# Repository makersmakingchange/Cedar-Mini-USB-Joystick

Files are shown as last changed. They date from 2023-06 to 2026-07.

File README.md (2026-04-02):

# Cedar Mini USB Joystick

## Overview

The Cedar Mini USB Joystick is a mini sized proportional joystick with integrated switch ports that can act as either an HID gamepad or as a mouse for adaptive gaming or computer access. Based on a generic PS2-style game controller thumbstick, it has range of motion of ±30° and requires approximately 75 grams-force to fully deflect. This joystick has a USB output cable and 3 ports for external assistive switches. 

The Cedar Mini USB Joystick can be used directly as a left or right thumbstick for the [Microsoft Xbox Adaptive Controller (XAC)](https://www.xbox.com/en-CA/accessories/controllers/xbox-adaptive-controller) using the Left and Right USB joystick ports in Joystick mode, or directly with a computer or mobile device.

A range of toppers are available for this joystick, including a [set of toppers created by AbleGamers Charity](https://www.printables.com/model/501869-analog-thumbstick-topper-collection).
 
The Cedar Mini USB Joystick is open assistive technology (OpenAT). Under the terms of the open source licenses, the device may be built, used, and improved upon by anyone.

The overall cost of materials is about $43 CAD (plus $8 CAD for component shipping).

The [Spruce Mini Joystick](https://github.com/makersmakingchange/Spruce-Mini-Joystick) is an alternative version of this joystick. It uses the same thumbstick component, but instead of USB output it has a TRRS cable for the joystick and a mono cable for the integrated joystick button. 

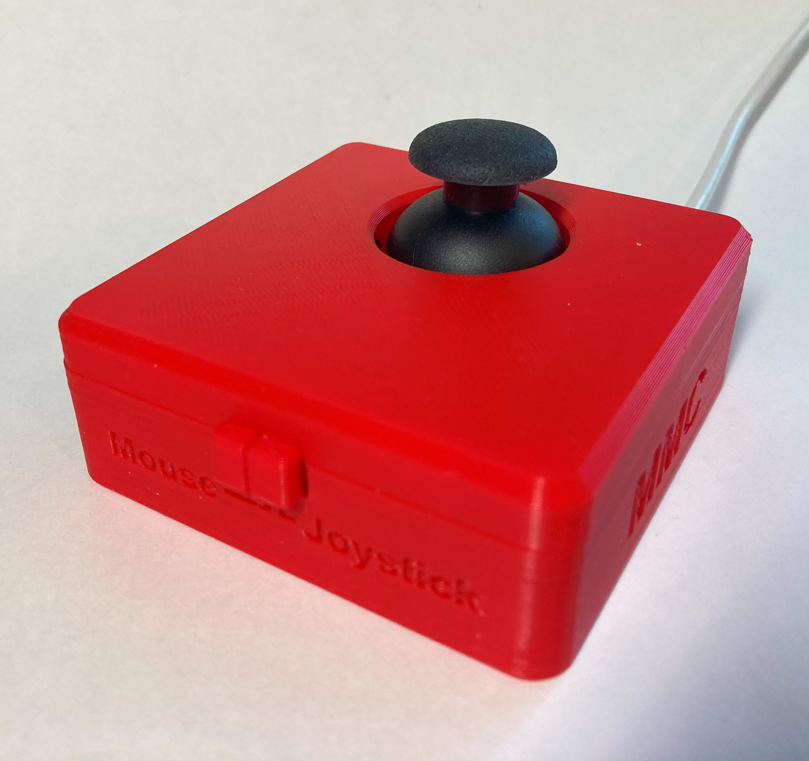
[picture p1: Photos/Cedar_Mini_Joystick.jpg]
Picture of Cedar Mini USB Joystick.


## Makers Making Change Assistive Device Library
https://www.makersmakingchange.com/s/product/cedar-mini-usb-joystick/01tJR00000092vRYAQ

## OpenAT Joysticks
This design is part of the [OpenAT Joystick project](https://github.com/makersmakingchange/OpenAT-Joysticks), a collection of open source designs for digital access and adapted gaming.  

## How to Obtain the Device
### 1. Do-it-Yourself (DIY) or Do-it-Together (DIT)

This is an open-source assistive technology, so anyone is free to build it. All of the files and instructions required to build the device are contained within this repository. Refer to the Maker Guide below.

### 2. Request a build of this device

You may also submit a build request through the [Makers Making Change Assistive Device Library Listing](https://www.makersmakingchange.com/s/product/cedar-mini-usb-joystick/01tJR00000092vRYAQ) to have a volunteer maker build the device. As the requestor, you are responsible for reimbursing the maker for the cost of materials and any shipping.

### 3. Build this device for someone else

If you have the skills and equipment to build this device, and would like to donate your time to create the device for someone who needs it, visit the [MMC Maker Wanted](https://makersmakingchange.com/maker-wanted/) section.

## Build Instructions
<!--- Outline the major steps required to create a build --->

### 1. Read through the Maker Guide

The [Maker Guide](/Documentation/Cedar_Joystick_Maker_Guide.pdf)  contains all the necessary information to build this device, including tool lists, assembly instructions, programming instructions (if applicable) and testing.

### 2. Order the Off-The-Shelf Components

The [Bill of Materials](/Documentation/Cedar_Joystick_BOM.csv) lists all of the parts and components required to build the device.

### 3. Print the 3D Printable components

All of the files and individual print files can be found in the [/Build_Files/3D_Printing_Files](/Build_Files/3D_Printing_Files/) folder.

Make sure to ask the user if they would like any of the optional prints such as toppers or mount adapters. Refer to the [OpenAT Joystick Setup Guide](https://github.com/makersmakingchange/OpenAT-Joysticks/Resources/OpenAT_Joystick_Setup_Guide.pdf) for detailed mounting options. 

### 4. Assemble the Cedar Mini USB Joystick

Reference the Assembly Guide section of the [Maker Guide](/Documentation/Cedar_Joystick_Maker_Guide.pdf) for the tools and steps required to build the device.

## How to improve this Device
As open source assistive technology, you are welcomed and encouraged to improve upon the design. 

## Files
### Documentation
<!--- Update the name, link, and version for documentation --->
| Document             | Version | Link |
|----------------------|---------|------|
| Design Rationale     | 1.0     | [Cedar_Joystick_Design_Rationale](/Documentation/Cedar_Joystick_Design_Rationale.pdf)     |
| Maker Guide          | 1.0     | [Cedar_Joystick_Maker_Guide](/Documentation/Cedar_Joystick_Maker_Guide.pdf)     |
| Bill of Materials    | 1.0     | [Cedar_Joystick_Bill_of_Materials](/Documentation/Cedar_Joystick_BOM.csv)     |
| User Guide           | 1.0     | [Cedar_Joystick_User_Guide](/Documentation/Cedar_Joystick_User_Guide.pdf)    |
| Changelog            | 1.0     | [Changelog](CHANGES.txt)     |

### Design Files
<!--- Include a copy of the original design files to facilitate easy editing and customization. Consider also including a generic format (e.g., STEP) --->
 - [CAD Files](/Design_Files/CAD_Design_Files)

### Build Files
<!--- Include a copy of the build files intended for manufacturing. This may include svg files for laser cutting, stl files for 3d printing, Gerber files for custom PCBs, and Arduino files for custom firmware. --->
 - [3D Printing Files](/Build_Files/3D_Printing_Files)
 - [Firmware Files](/Build/Firmware_Files)

## License
Copyright (c) 2023-2026 Neil Squire Society.

This repository describes Open Hardware:
 - Everything needed or used to design, make, test, or prepare the Cedar Mini USB Joystick is licensed under the [CERN 2.0 Weakly Reciprocal license (CERN-OHL-W v2) or later](https://cern.ch/cern-ohl ) .
 - All software is under the [GNU General Public License v3.0 (GPL-3.0)](https://www.gnu.org/licenses/gpl.html).
<<<<<<< Updated upstream
 - Accompanying material such as instruction manuals, videos, and other copyrightable works that are useful but not necessary to design, make, test, or prepare the Cedar USB Joystick are published under a [Creative Commons Attribution-ShareAlike 4.0 license (CC BY-SA 4.0)](https://creativecommons.org/licenses/by-sa/4.0/) .
=======
 - Accompanying material such as instruction manuals, videos, and other copyrightable works that are useful but not necessary to design, make, test, or prepare the Cedar Joystick are published under a [Creative Commons Attribution-ShareAlike 4.0 license (CC BY-SA 4.0)](https://creativecommons.org/licenses/by-sa/4.0/) .
>>>>>>> Stashed changes

You may redistribute and modify this documentation and make products using it under the terms of the [CERN-OHL-W v2](https://cern.ch/cern-ohl).
This documentation is distributed WITHOUT ANY EXPRESS OR IMPLIED WARRANTY, INCLUDING OF MERCHANTABILITY, SATISFACTORY QUALITY AND FITNESS FOR A PARTICULAR PURPOSE.
Please see the CERN-OHL-W v2 for applicable conditions.

Source Location: https://github.com/makersmakingchange/Cedar-Mini-USB-Joystick 

## Attribution
<!--- Provide any necessary attribution for designs or components that are included in the device or as part of the project. --->
The device was designed by the Neil Squire Society / Makers Making Change Program. 

The software utilizes the [Adafruit TinyUSB Library for Arduino](https://github.com/adafruit/Adafruit_TinyUSB_Arduino) which is made available under an [MIT license](https://github.com/adafruit/Adafruit_TinyUSB_Arduino/blob/master/LICENSE).

A range of toppers are availablef or this joystick and utilize the mofels found in the [set of toppers created by AbleGamers Charity](https://www.printables.com/model/501869-analog-thumbstick-topper-collection).

<!--- This is the attribution for the template. --->
This project uses the documentation template created by Neil Squire Society / Makers Making Change. It is available at the following link: [https://github.com/makersmakingchange/OpenAT-Template](https://github.com/makersmakingchange/OpenAT-Template)

### Contributors
<!--- List the names of the people that contributed to the design. This could include the original source of the idea, designers, testers, documenters, etc. --->
Designers:
 - Josie Versloot, Neil Squire Society. Hardware and enclosure design, software, documentation.
 - Milad Hajihassan, Neil Squire Society. Software.
 - Emily Schwitz, Neil Squire Society. Documentation.
 - Tyler Fentie. Documentation, Editing.
 - Jake McIvor. Documentation, testing, editing.

---
<!--- This is standard boilerplate for Makers Making Change. No changes should be required. --->
<!-- ABOUT MMC START -->
## About Makers Making Change
[Makers Making Change Logo](https://www.makersmakingchange.com/)

Makers Making Change is a program of [Neil Squire](https://www.neilsquire.ca/), a Canadian non-profit that uses technology, knowledge, and passion to empower people with disabilities.

Makers Making Change leverages the capacity of community based Makers, Disability Professionals and Volunteers to develop and deliver affordable Open Source Assistive Technologies.

 - Website: [www.MakersMakingChange.com](https://www.makersmakingchange.com/)
 - GitHub: [makersmakingchange](https://github.com/makersmakingchange)
 - Bluesky: [@makersmakingchange.bsky.social](https://bsky.app/profile/makersmakingchange.bsky.social)
 - Instagram: [@makersmakingchange](https://www.instagram.com/makersmakingchange)
 - Facebook: [makersmakechange](https://www.facebook.com/makersmakechange)
 - LinkedIn: [Neil Squire Society](https://www.linkedin.com/company/neil-squire-society/)
 - Thingiverse: [makersmakingchange](https://www.thingiverse.com/makersmakingchange/about)
 - Printables: [MakersMakingChange](https://www.printables.com/@MakersMakingChange)

### Contact Us
For technical questions, to get involved, or to share your experience we encourage you to [visit our website](https://www.makersmakingchange.com/) or [contact us](https://www.makersmakingchange.com/s/contact).
<!-- ABOUT MMC END -->

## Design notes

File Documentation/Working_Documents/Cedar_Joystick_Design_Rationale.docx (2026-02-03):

# Overview

The Design Rationale is intended to provide designers and maker information about the design process and design decisions behind the development of the Cedar USB Joystick, a joystick with switch ports.

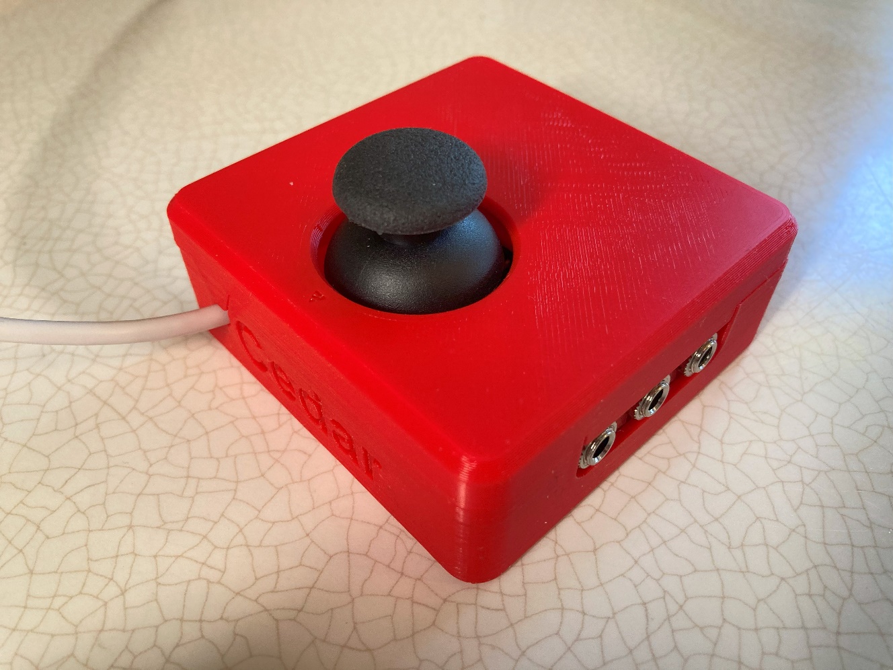
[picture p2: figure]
A photo of a fully assembled Cedar USB Joystick.

# Contents

# Introduction

There is an identified need for cost-effective analog joysticks that can be used with the Xbox Adaptive Controller (XAC). There are currently not very many commercial joysticks on the market, and the ones that are can be costly. This joystick is intended to be used with the XAC for anyone who may find it easier to game with a joystick.

There is also a need for alternative mouse options that are affordable, and some people may find a joystick easier to use than a mouse. This mouse needs to be a standalone device that can be used with PC and can complete the basic mouse functions such as left click.

This joystick specifically is meant for someone with a lower range of motion and lower force compared to some USB joysticks.

# Research

## Commercial Joysticks:

Name | Price | | Link | | | Picture
Ultra-Stik | 95 UK | | Accessible Gaming Shop - Ultra-Stik - OneSwitch.org.uk (https://www.oneswitch.org.uk/art.php?id=17)
XAC MINI Stick | 105 UK | | XAC Mini Joystick - OneSwitch.org.uk (https://www.oneswitch.org.uk/art.php?id=270)
Optima Joystick | 219.60 UK | | Optima Joystick - Video Gaming Assistive Joystick (pretorianuk.com) (https://www.pretorianuk.com/optima-joystick)
PDP One-Handed Joystick for Xbox Adaptive Controller | Out of Stock | | PDP One-Handed Joystick for Xbox Adaptive Controller (microsoft.com) (https://www.microsoft.com/en-ca/d/pdp-one-handed-joystick-for-the-xbox-adaptive-controller/8qhw8mlwpp1l)
XAC Flat Thumbstick | $74.95 | | XAC Flat Thumbstick (evilcontrollers.com) (https://www.evilcontrollers.com/xac-flat-thumbstick)
Name | | Price | | Link | Picture
MINISTIX-TU | | $75 | | MINISTIX-TU (USB Version) — Warfighter Engaged (https://warfighterengaged.org/shop/ministix-tu)
DPAD-T | | $65 | | DPAD-T — Warfighter Engaged (https://warfighterengaged.org/shop/dpad-t)
JOYSTIX-FPS | | $75 | | JOYSTIX-FPS — Warfighter Engaged (https://warfighterengaged.org/shop/joystix-l-aenef)
JoyCon® Style Joystick For XBOX® Adaptive Controller & PC (JoyToKey) | | $60.40 | | Joycon® Style Joystick for XBOX® Adaptive Controller & PC | Etsy Canada (https://www.etsy.com/ca/listing/1205880837/joycon-style-joystick-for-xbox-adaptive?click_sum=ba40a784&crt=1)

# Ideation

## Joystick Element

For this design, the same joystick element will be used as the current Analog Thumbstick on the website, which is a standard PS2 thumbstick unit.

## Switch Input

There are a few different ways that switch input can be accomplished:

- Integrated buttons
- Integrated switch jacks
- Separate “controller box” that the joystick and switches plug into

For this design, it was decided to use integrated switch jacks, where the user can plug in their assistive switch of choice for switch input. While in mouse mode, these switches will be left click, right click, and middle click (scroll).

This decision will be further investigated and specifically asked about in user testing.

# Conceptual Design

## Electrical Design

### Microcontroller

The microcontroller used in this design is the Adafruit QT Py SAMD21.

Originally the Seeed Studio XIAO RP2040 was going to be used since it is the microcontroller used in the Oak Compact Joystick – U and the Birch Mini joystick – U, but during development and testing there were problems reading the switch inputs. From what we read online; this was likely due to the pullup resistors. Documentation for the XIAO RP2040 is not consistent, some sources say it has pullup resistors and others say it does not. After this realization, both the Adafruit QT Py SAMD21 board and the Seeed Studio XIAO SAMD21 boards were tested since they both have the same footprint as the XIAO RP2040 board. The Seeed Studio XIAO SAMD21 board had problems with the Adafruit TinyUSB library, after looking online this is a known problem, but the solution of using an older version of the TinyUSB library did not work either. The Adafruit QT Py SAMD21 board, however, seemed to work well, so the final decision was to use this board even though on Digikey it is approximately $3 more.

### Switch Inputs

This design will use switch jacks integrated into the body of the joystick. There will be 3 switch jacks, which in mouse mode will represent left click, right click, and middle click.

From initial conversations with clinicians and users, it was determined that these three inputs are all very important. The ability to easily scroll is sometimes overlooked but the importance of this was expressed to us, so this will be accomplished through the middle click button.

### Mode Switch

A 3-way slide switch to switch between mouse mode and joystick mode, will also be included in this design. This is so that either the user or secondary user (such as a support person) can easily change the mode to use this joystick as either a joystick or mouse. This method of mode switching does not require the user or secondary user to have any knowledge of code or software, and allows this mode switch to happen easier than if the joystick and mouse used separate versions of the code.

The selection of which switch exactly will be used will depend on the method of electronical component mounting and wiring, decided below. This will dictate whether the slide switch needs to be panel mounted, breadboard friendly, right angled, etc.

Example of a breadboard friendly slide switch:

https://www.adafruit.com/product/805

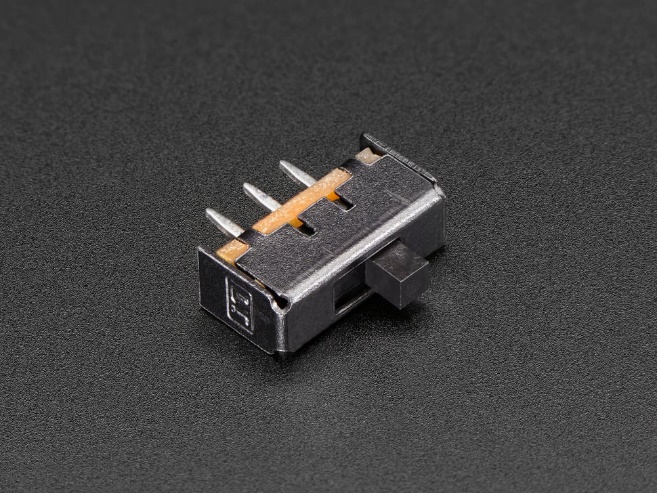
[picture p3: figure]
Breadboard-friendly SPDT Slide Switch

### Electrical Component Wiring and Mounting

For mounting the electrical components and wiring the components together, there are a few options to accomplish this:

1. Components mounted directly in 3D printed enclosure (panel mount switch jacks and slide switch)
2. 3D printed PCB/3D printed jig
3. Protoboard with breadboard friendly jacks
4. Combination of protoboard and panel mounts
5. Printed Circuit Board (PCB)

With each of these options there are a few different factors to consider:

- Ease of assembly for the maker
- Device cost
- Design complexity
- Device size

For each of these concepts the following components need to be included:

- Microcontroller
- Joystick Module
- 3x Switch Jack
- Slide Switch

#### Concept 1: Components mounted directly in 3D printed enclosure

This would use panel mount components for the slide switch and switch jacks, and would involve mounting the microcontroller directly in the enclosure. Wiring would be completed with free floating wires.

Easy of assembly: a lot of free floating wires, tricky to hold while soldering, tricky to keep them all straight, would need to daisy chain multiple ground wires together. If soldering while the components are mounted it could be hard to get in to solder, but if the components are free there is risk the wires may not reach.

Device cost: lower cost due to not having to buy protoboard or a PCB. Other components similar in price.

Design complexity: easy to design, easy to mount components where they fit best. Will need to consider how to mount the micro controller.

Device size: allows the device to be relatively compact since components can be placed anywhere in the enclosure that thy fit best.

#### Concept 2: 3D printed PCB/3D printed jig

This would involved a 3D printed board that the components would be mounted to and would help guide the wiring.

This could be similar to the Switch Input Module for the LipSync:

Female headers could be embedded in the 3D print for mounting the microcontroller and this could help guide the wires for connecting the switch jacks and slide switch to the microcontroller, and would likely be easier than free hanging wires. The switch jacks, slide switch, and microcontroller could all be mounted on this board, and the board could have any shape needed to fit in the enclosure and fit around the joystick component. There could be female headers that fit onto the male headers on the joystick board.

Ease of assembly: Likely easier than free hanging wires in Concept 1, but more complex than a PCB. The print would help guide the positioning and wiring of the various components.

Device cost: lower cost due to not having to buy protoboard or a PCB. Other components similar in price.

Design complexity: Relatively complex, positioning and wiring of each component needs to be considered in the board. Pieces need to fit properly.

Device size: allows the device to be compact since the printed board can take on any necessary shape.

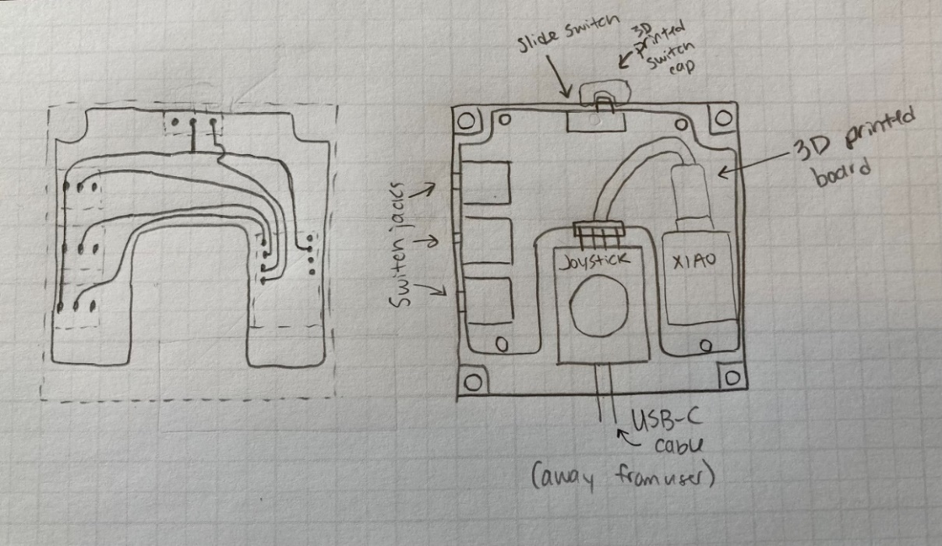
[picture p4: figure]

This concept was also tested out in CAD to see the real size of components relative to each other. This was the first attempt at laying out the components:

#### Concept 3: Protoboard with breadboard friendly jacks

Ease of assembly: Likely easier than concept 1 with the panel mounted components and free floating wires, and slightly easier than the 3D printed PCB, but likely somewhat comparable. If using stripboard, this will be more simple, but if using protoboard with individual pads this will be more complex as it will require solder bridges.

Device cost: Added cost of the protoboard. Depending on the board this could range from $2 to $6. Other components should be similar in price.

Design complexity: Relatively simple design, if the protoboard has screw holes these can be incorporated, otherwise will need to think about mounting the protoboard.

Device size: This depends on if using stripboard or single pad protoboard, but with stripboard as seen below space cannot be as optimized since the pads are connected, dictating where components can and cannot go. If using single pad protoboard, the design can be more compact, but this adds assembly complexity.

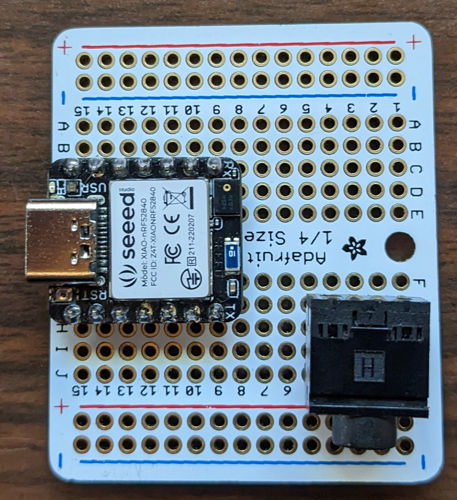
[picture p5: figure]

https://www.adafruit.com/product/589

3 breadboard friendly audio jacks could fit along one side of a quarter sized proto board, or the SeeedStudio XIAO board (same footprint as Adafruit AT Py) could fit along with 2 breadboard friendly audio jacks.

Another concept that was experimented with was using two protoboard with individual pads (rather than strip board) and attaching the two boards together using right angle male and female headers.

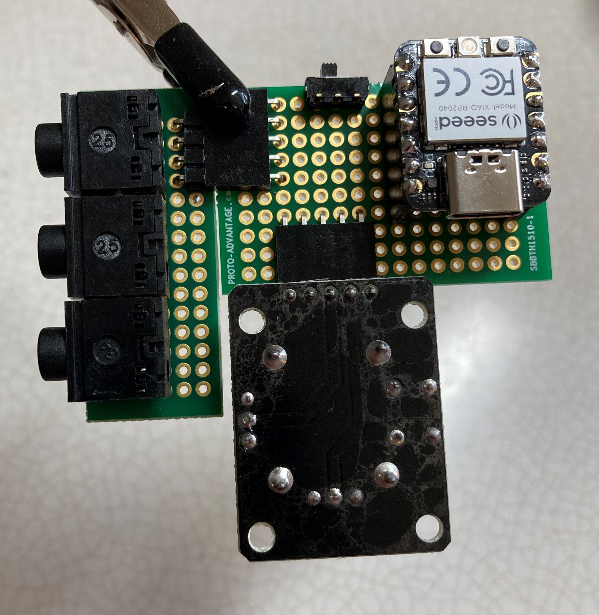
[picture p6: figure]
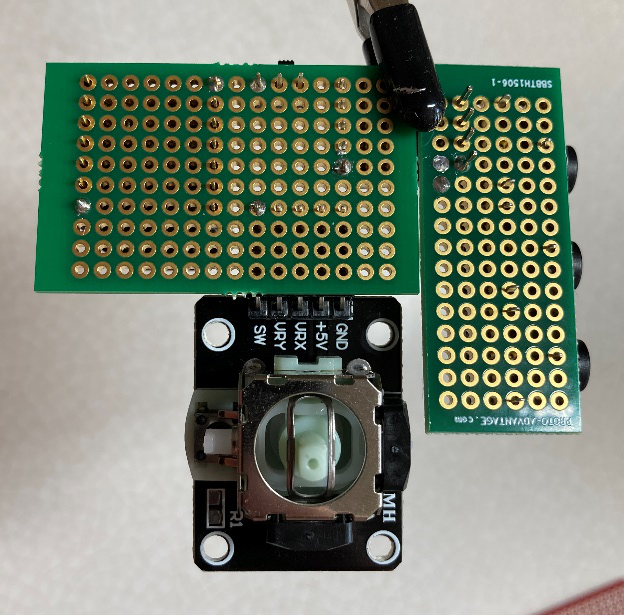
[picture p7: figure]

This concept has promise since it is relatively compact, and having the components on the “underside” of the protoboard decreases the height of the enclosure significantly. However, with these protoboards there is still the challenge of mounting them since they do not have screw holes, and they would need to be secure since the user would be plugging and unplugging switches from the mono jacks. Additionally, since it uses individual pads instead of stripboard, wiring would likely require solder bridges which means assembly would not be much easier than the 3D PCB.

#### Concept 4: Combination of protoboard and panel mounts

This concept would allow for the use of a smaller protoboard than concept 3, since not all components would need to be mounted on it. For example, the microcontroller and slide switch could mount to the protoboard and the mono jacks could be panel mounted. Another possibility is having the mono jacks and slide switch on the protoboard and then having the microcontroller mounted to the enclosure directly. This can also allow for a more compact layout than concept 3 if using one protoboard.

Ease of assembly: Slightly easier than concept 1 with all panel mounted components, but more difficult than concept 3 with a protoboard.

Device cost: Similar to concept 4, more than concept 1 and 2 due to added cost of protoboard.

Design complexity: Relatively simple, depending on the mounting of the protoboard.

Device size: Allows the enclosure to be more compact than concept 3 (if only using one board) since the layout of the parts is not defined by the size and layout of the protoboard.

#### Concept 5: Printed Circuit Board (PCB)

Ease of assembly: This would be the easiest of the options in terms of assembly, since the components could just be soldered to the board and wires would not need to be added between components. There would also be less room for error while assembling with this option.

Device cost: Adds approximately ~$30 to cost for a single build

Design complexity: It takes time to prototype, order, and test PCB boards, so the design complexity is likely too high for the timeline of the initial design.

Device size: A custom PCB can be made in any shape, therefore allowing the size to be relatively compact.

Discussion: One PCB design could be used across different devices.

#### Selection

For the initial version of this design, version 0.9, concept 2 with the 3D printed circuit board was selected. This option is easier to assemble than concept 1; lower cost than concept 3, 4, and 5; and is only marginally more difficult to assemble than concept 3. Though concept 5 would be easier to assemble, the cost is much higher, and the design time is not feasible for this design iteration.

There is a possibility of creating a PCB at a later stage in the design process, and having two options for the build depending on if someone is building one or multiple. When building multiple joysticks, the cost of the PCB per joystick drops significantly, making it a more viable option when doing bulk orders.

While designing the 3D printed circuit board, the idea of implementing concept 5 at a later date will be kept in mind, and the 3D printed circuit board will be designed to be able to easily transition to a custom ordered PCB at a later date.

## Firmware Design

For this joystick, the joystick mode and mouse mode will be captured on one firmware, with a slide switch to switch between modes. This switch will be checked once upon startup, and will determine if the device will be set up as a joystick/HID gamepad or as a mouse. If switching between joystick and mouse mode, the device will need to be unplugged and plugged back into the host device.

For both joystick and mouse output, there is a deadzone where if the joystick readings are below a certain value, the output will be zero. This code uses a radial deadzone, which if mapped would have a circular shape, and the radius of this deadzone is set in a variable at the start of the code. If the joystick is experiencing drift, this deadzone may need to be increased. If small movements are not corresponding to outputs, this value may need to be decreased.

### Joystick Mode

For the joystick mode portion of the code, the code from the MMC OpenAT Joysticks, the Birch Mini Joystick – U and the Oak Compact Joystick – U will be used and modified. The main changes from this code will be incorporating the switch inputs and modifying the code to work with the Adafruit QT Py SAMD21 microcontroller.

This joystick has three accessible switch jacks, and has one built in switch in the joystick that is activated when the joystick is pressed down. These switches will be mapped as buttons 1 to 4 on the gamepad output.

### Mouse Mode

For the mouse mode portion of the code, the mouse functions were added into the joystick code, with conditional statements so they are only outputted when in mouse mode. The three switch jacks (labelled A, B, C from left to right) are mapped as left click, middle click (for scroll), and right click (from left to right). The joystick press down button is mapped to left click.

Since the joystick portion of the code requires the use of the Adafruit TinyUSB stack, and the typical Mouse.h library uses the Arduino USB stack, an alternative library had to be used that allowed for Mouse functionality with the TinyUSB stack. This library was found on GitHub by user cyborg5 (https://github.com/cyborg5/TinyUSB_Mouse_and_Keyboard).

## Mechanical Design

The mechanical design is largely dependant on the electrical component wiring and mounting. After selecting concept 2 for the electrical design, the enclosure and 3D PCB could be designed. The current Analog Thumbstick on the MMC library has a footprint of 69 mm by 69 mm, so effort will be made for this new enclosure design to be similar in size.

In this enclosure, it will be ensured that the mono jacks and slide switch are mounted in a way that is very secure since the user will be applying forces to these parts.

The enclosure will also include captive M3 nuts to be used with the MMC Joystick camera mount adapter.

The current Analog Thumbstick on the MMC library uses 4 screws to secure the enclosure, and 4 screws to secure the joystick to the enclosure. This approach will be used for this enclosure as well, for both simplicity of design, and strength of the connection. Since the user will be applying forces to the joystick that could be quite large, this needs to be mounted to the enclosure in a strong and secure way. Relying on snap fits can also be difficult if printer tolerances are very different. This enclosure, like the Analog Thumbstick, will use 8 size 4-24 self threading sheet metal screws. The 3D PCB will be secured using the same screws as the ones holding together the enclosure.

# Minimum Viable Product – V0.9

## Summary

- Cost
  - Unit cost: $42.74 ($34.74 for parts, $8 shipping)
  - Total maker cost: $64.33 ($56.33 for parts, $8 shipping)
- Print time: 4 hours 53 mins
- Total 3D printer filament used: 41 g
- Approximate build time: 1 hour??
- Size:
  - Total Height: 4.0 cm with original topper
  - Enclosure height: 2.7 cm
  - Width: 7.0 cm
  - Length: 7.0 cm

### Bill of Materials

The following components were selected based on price, availability, and components used internally for MMC designs.

Part Name | QTY | QTY /PKG | $/PKG | PKG QTY | $/Unit | Extended | Total
Joystick (PS2) (https://www.amazon.ca/dp/B089VXPHDH?_encoding=UTF8&psc=1&ref_=cm_sw_r_cp_ud_dp_GGTEDME4PM2P27SG86P7) | 1 | 10 | $ 23.99 | 1 | $ 2.40 | $ 2.40 | $ 23.99
USB-C cable, 6 ft (https://www.digikey.ca/en/products/detail/cvilux-usa/DH-20M50053/13177348) | 1 | 1 | $ 3.18 | 1 | $ 3.18 | $ 3.18 | $ 3.18
Adafruit QT Py SAMD21 (https://www.digikey.ca/en/products/detail/adafruit-industries-llc/4600/13543375) | 1 | 1 | $ 10.79 | 1 | $ 10.79 | $ 10.79 | $ 10.79
3.5 mm mono jack, panel mount (https://www.digikey.ca/en/products/detail/cui-devices/MJ-3502/281321) | 3 | 1 | $ 2.32 | 3 | $ 2.32 | $ 6.96 | $ 6.96
Slide switch, right angle (https://www.digikey.ca/en/products/detail/c-k/OS102011MA1QS1/1981431) | 1 | 1 | $ 0.75 | 1 | $ 0.75 | $ 0.75 | $ 0.75
Right angle female header, 5 position (https://www.digikey.ca/en/products/detail/sullins-connector-solutions/PPTC051LGBN-RC/775899) | 1 | 1 | $ 0.93 | 1 | $ 0.93 | $ 0.93 | $ 0.93
Female header, 7 position, single row, 0.100" (https://www.digikey.ca/en/products/detail/sullins-connector-solutions/PPTC071LFBN-RC/810146) | 2 | 1 | $ 0.85 | 2 | $ 0.85 | $ 1.70 | $ 1.70
#4 Metal Screw, 3/8″ Length (https://www.digikey.ca/en/products/detail/serpac/6005/307599) | 8 | 1 | $ 0.60 | 8 | $ 0.60 | $ 4.80 | $ 4.80

Wire, 1 foot, colour 1 (https://www.digikey.ca/en/products/detail/cnc-tech/3122-24-1-0500-007-1-TS/16396741) | 1 | 1 | $ 0.70 | 1 | $ 0.70 | $ 0.70 | $ 0.70
Wire, 1 foot, colour 2 (https://www.digikey.ca/en/products/detail/cnc-tech/1569-26-1-0500-003-1-TS/15853701) | 1 | 1 | $ 0.72 | 1 | $ 0.72 | $ 0.72 | $ 0.72
Ziptie (https://www.digikey.ca/en/products/detail/te-connectivity/2-604771-9/2259327) | 1 | 1 | $ 0.25 | 1 | $ 0.25 | $ 0.25 | $ 0.25
M3 hex nut x2 (https://www.digikey.ca/en/products/detail/b-f-fastener-supply/MHNZ-003/274973) | 2 | 1 | $ 0.27 | 2 | $ 0.27 | $ 0.54 | $ 0.54
(Optional for mount) M3x12mm screw x2 (https://www.digikey.ca/en/products/detail/apm-hexseal/RM3X12MM-2701/2063201) | 0 | 1 | $ 1.11 | 0 | $ 1.11 | - | -
(Optional for mount) Tee nut (https://www.homedepot.ca/product/paulin-1-4-inch-20-tee-nuts-4-prong-5-16-inch-barrel-length/1000129429) | 0 | 1 | $ 0.48 | 0 | $ 0.48 | - | -
Digikey shipping (if spending less than $100) | 1 | 1 | $ 8.00 | 1 | $ 8.00 | $ 8.00 | $ 8.00

## Detailed Design

### Electrical Design

#### Component Layout and Wiring

From the initial concept above, the 3D printed circuit board was created. The mono jacks will come out of the left side (from the user’s point of view), the slide switch will face the user, and the USB cable from the microcontroller will come out of the enclosure away from the user. The three screw holes in the corner are positioned to fit onto posts in the enclosure and “sandwich” between the top and bottom of the enclosure, using the same screws.

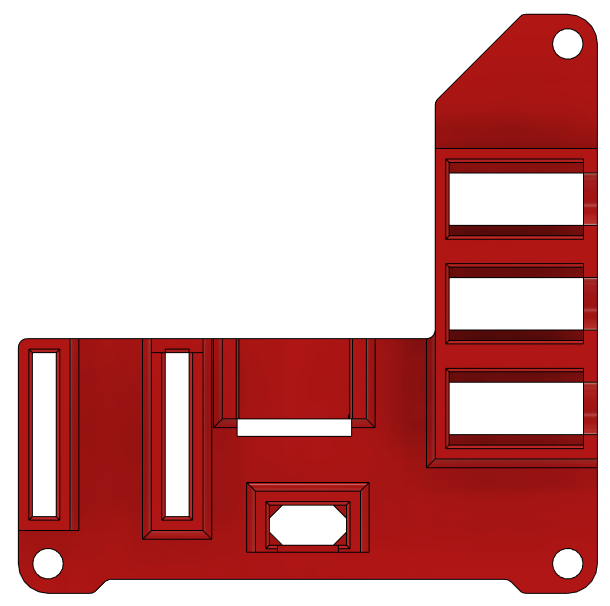
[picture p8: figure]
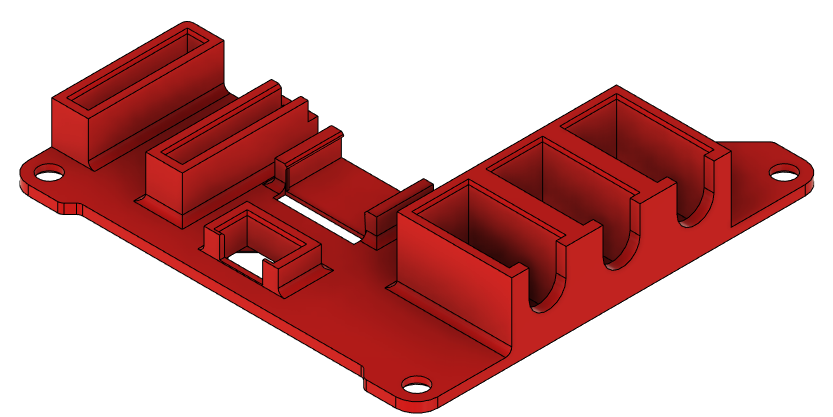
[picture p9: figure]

7 pin female headers for the microcontroller were included for ease of assembly, and ease of changing the microcontroller out if needed. These are press fit into the 3DP circuit board. For the joystick, there is a 5 pin right angle female header, and this is press fit into the enclosure with small bumps to keep it in place while wiring.

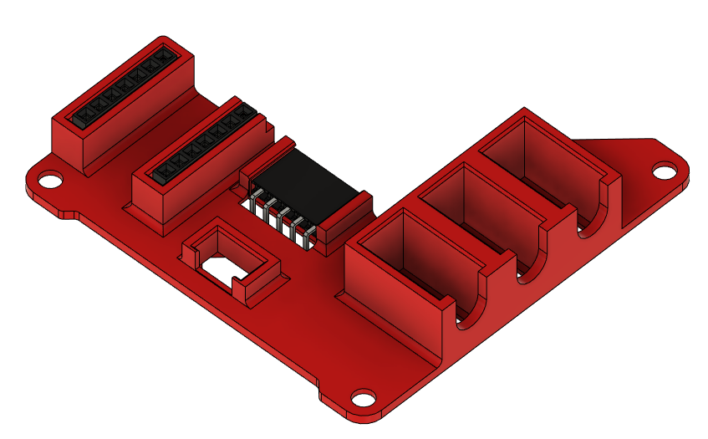
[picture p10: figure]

The microcontroller (with male headers soldered to it) then presses into the female headers to secure it in place. The joystick right angle headers slide into the female right angle headers. The slide switch is press fit into the surrounding 3D print, and has some material in the corners on the bottom to prevent it from going “through” the board. The mono jacks are a looser fit, but have panel mounts to keep them in place. There is also material on the bottom of the mono jacks to keep them from going “through” the board. In the picture below, the board is upside down, in reality the joystick will be rightside up and all the other parts will be upside down, this was to reduce the overall height of the enclosure.

The below picture is an earlier iteration of the design, but shows the nuts installed on the mono jacks to keep them in place.

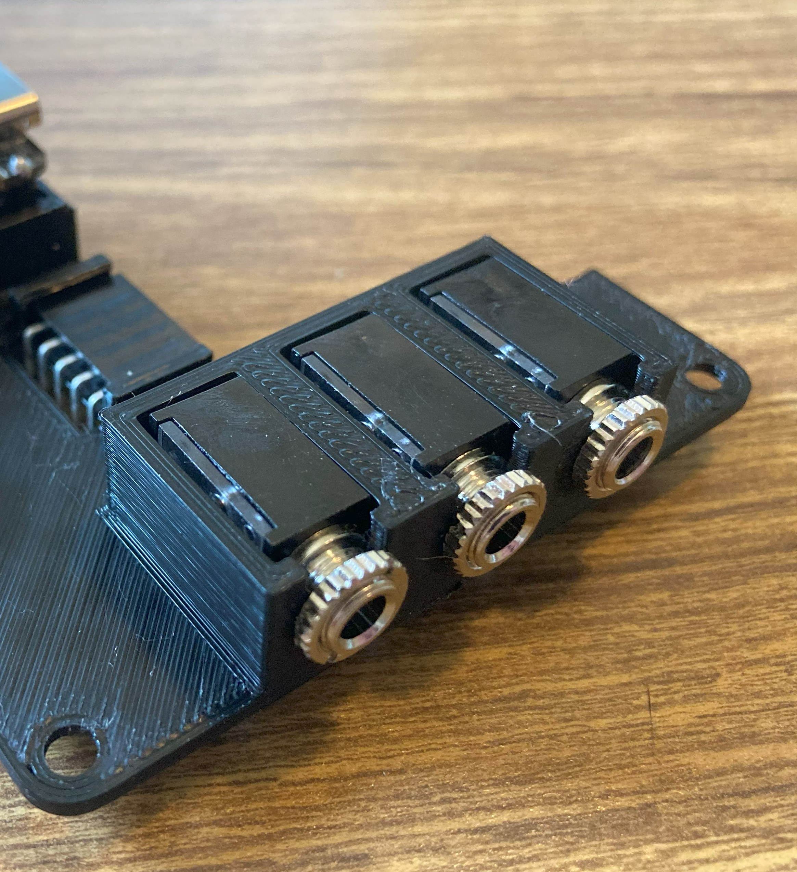
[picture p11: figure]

Below the board is rightside up, all of the leads to the electrical parts are facing upwards, and this is where the wires would be soldered.

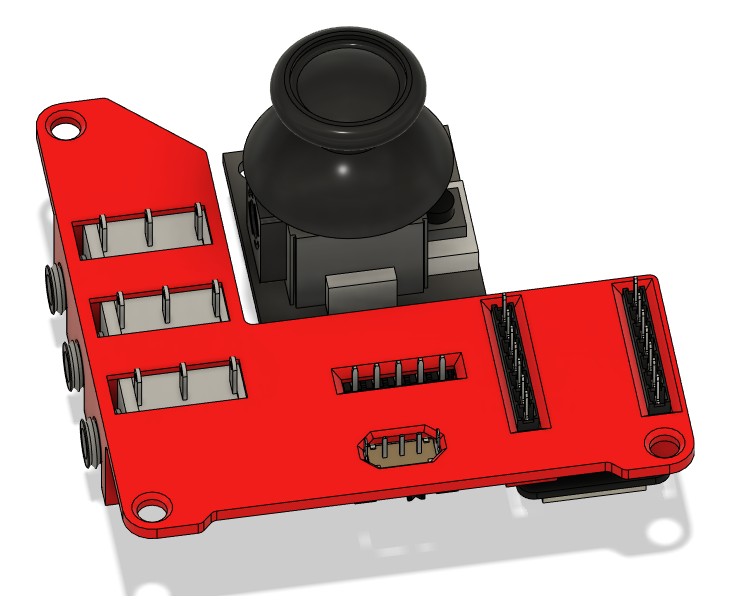
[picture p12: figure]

Below is a diagram showing the wiring of the electronics, for the joystick X and Y, analog pins had to be used, but for the rest the digital pins could be changed if it made wiring easier.

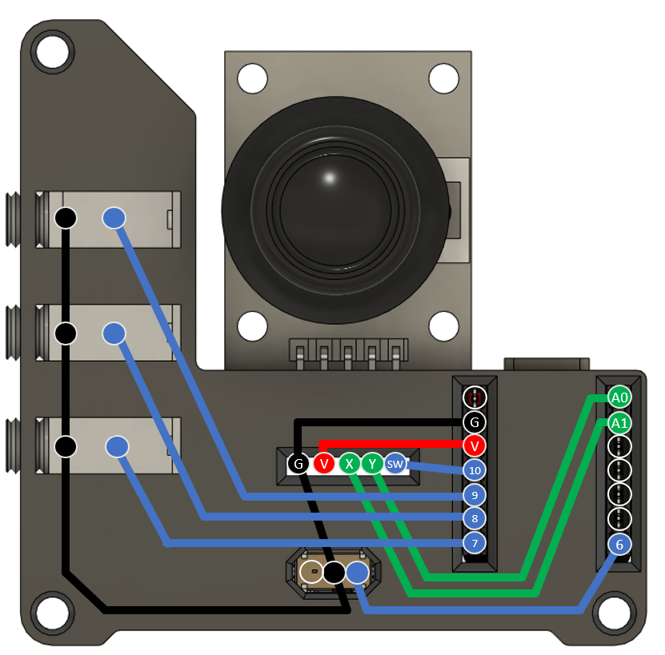
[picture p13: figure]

The wiring isn’t the easiest, and this could be improved, there are also some wired that must go on top of other wires, which if not done carefully could get messy.

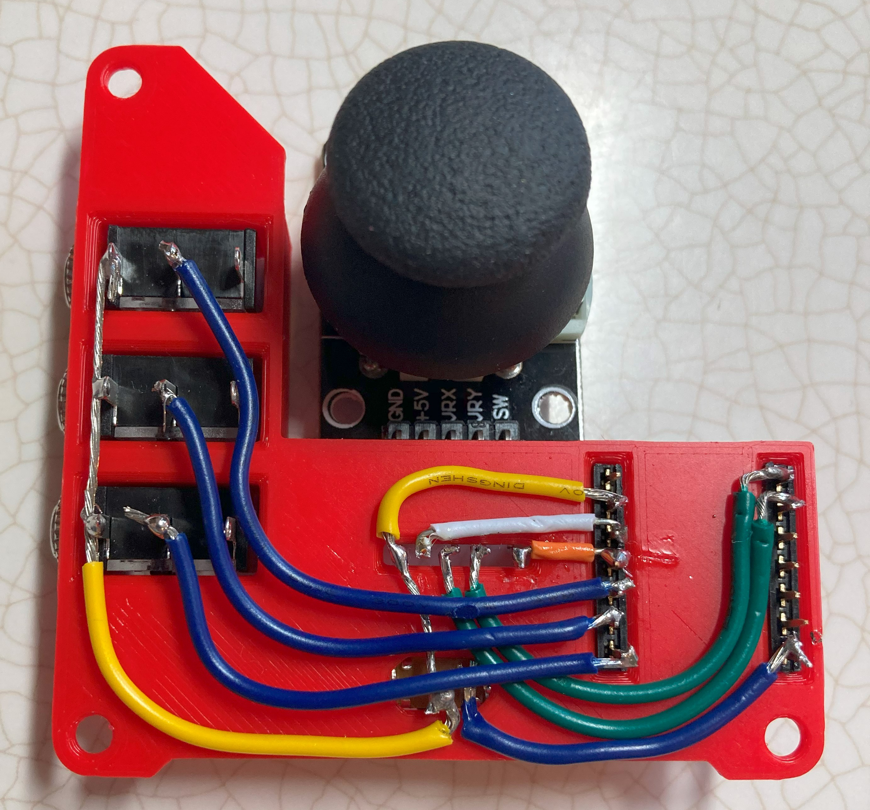
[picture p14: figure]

### Mechanical Design

#### Overview

On the outside of the enclosure, there are a few key features. On the side facing the user, is the mode selection slide switch and the works “Mouse” and “Joystick” showing the positions for the two modes. On the right side of the enclosure “MMC” is engraved.

On the left side are the three mono jacks, labelled A, B, C from left to right. On the side facing away from the user is the USB cable exit and the name of the joystick “Cedar” is engraved.

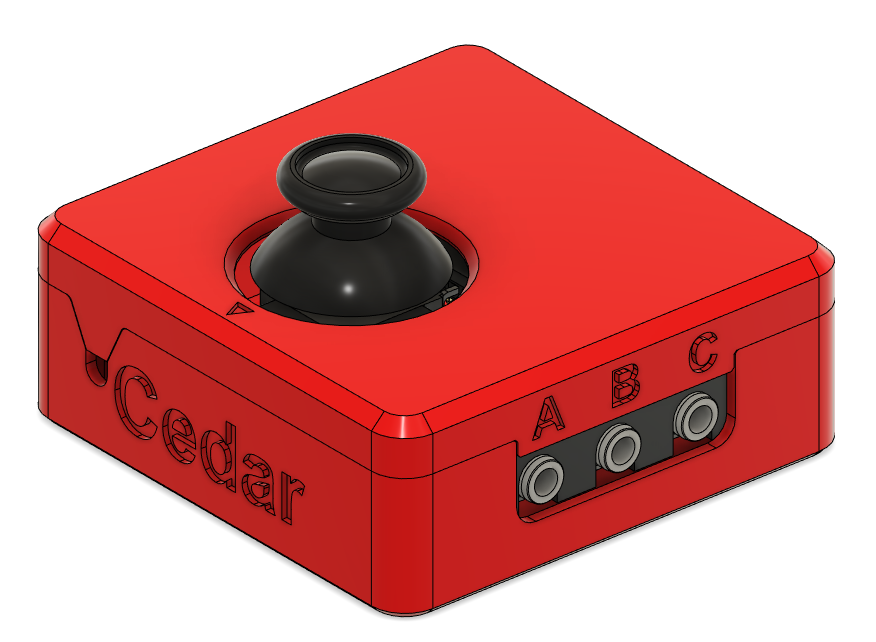
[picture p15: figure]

On the top of the joystick is a small triangle arrow, which points in the “up” direction of the joystick.

#### Assembled Prototype

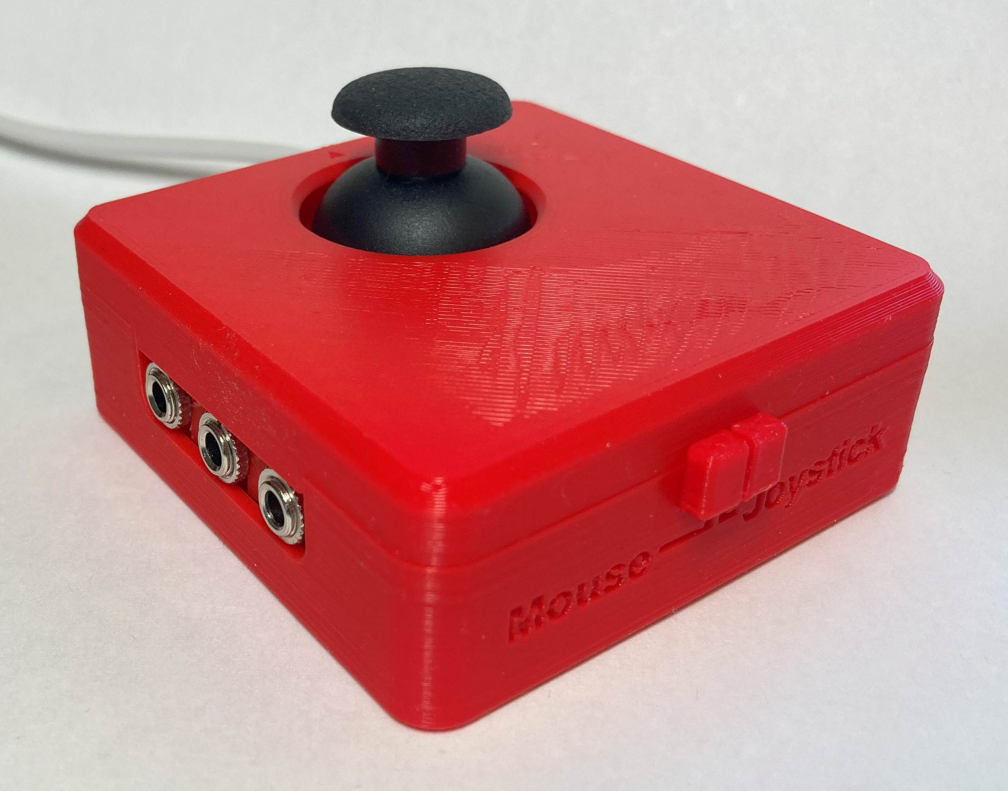
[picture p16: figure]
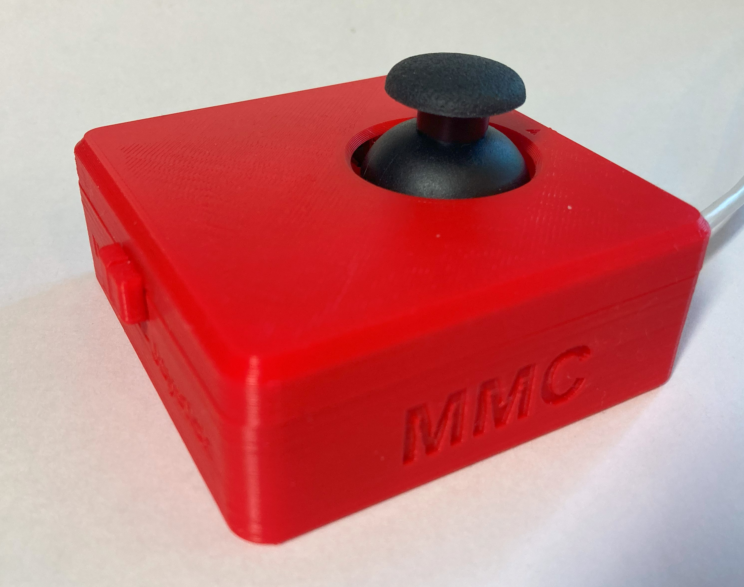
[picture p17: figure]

#### Enclosure Bottom

##### Joystick Mounting

In the bottom of the joystick there are four posts to mount the joystick with holes that are 2.68 mm in diameter. They fit self tapping sheet metal screws, size 4-24.

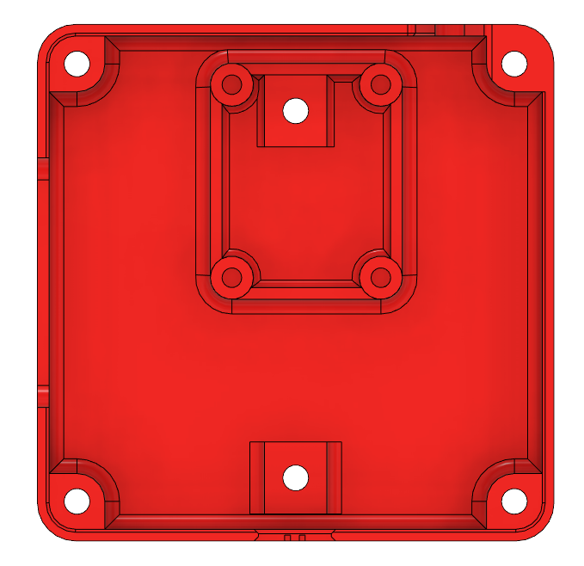
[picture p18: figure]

For this joystick in particular, which is linked in the Bill of Materials, this is the hole spacing:

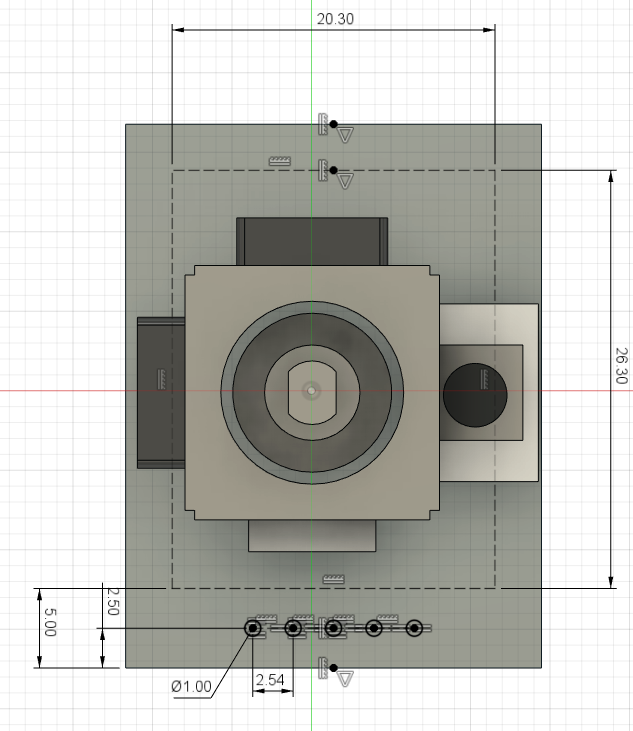
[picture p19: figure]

Hole spacing: 20.3 mm x 26.3 mm

##### Mounting – Captive nuts

It was decided that this design should incorporate a way to mount the joystick when not used on a tabletop. To do this, two slots for captive nuts were added, which would then screw into a separate mount adapter which will have the mounting hardware in it. Here, two M3 hex nuts are used. The centres of these nuts are 50.0 mm apart. These two slots are seen in the photos above, and then in a closer view below. As seen in the photo, around the hole above the captive nut, which would be printed unsupported, there are small single layer rectangles, this is a best practice when 3D printing unsupported holes. (https://www.hydraresearch3d.com/design-rules)

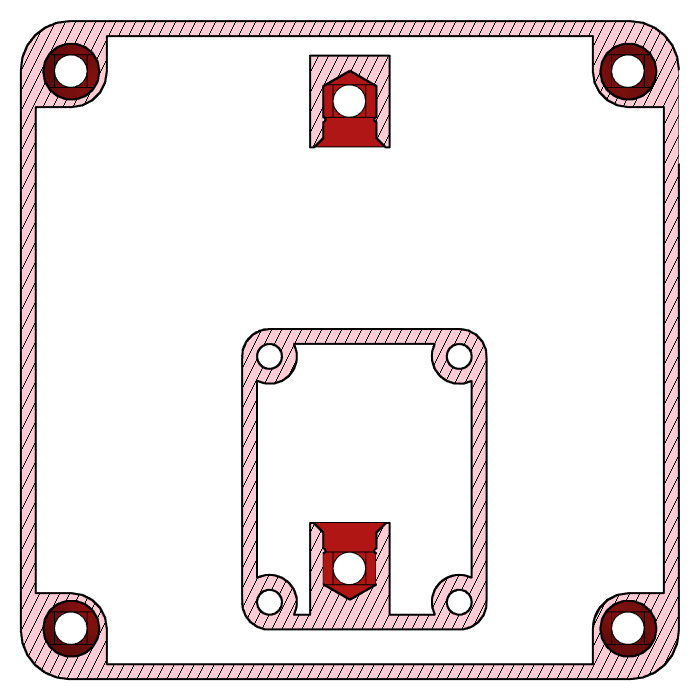
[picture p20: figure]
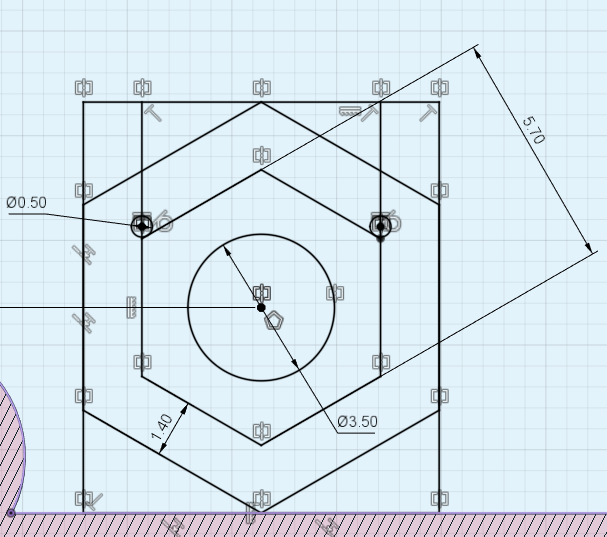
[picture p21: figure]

50mm

##### 3D Printed Circuit Board Mounting and Cutouts

To mount the 3D Printed Circuit Board, the existing screw holes to assemble the enclosure will be used. The posts with the screw holes were made shorter by 2.0 mm for the three posts that will hold the PCB, this is for the 1.6 mm thickness of the board plus 0.4 mm of clearance to account for printer tolerances and surface roughness so that there isn’t a gap between the top and bottom of the enclosure. The board sits on top of these posts, and there are cut-outs for the mono jacks to fit and for the slide switch.

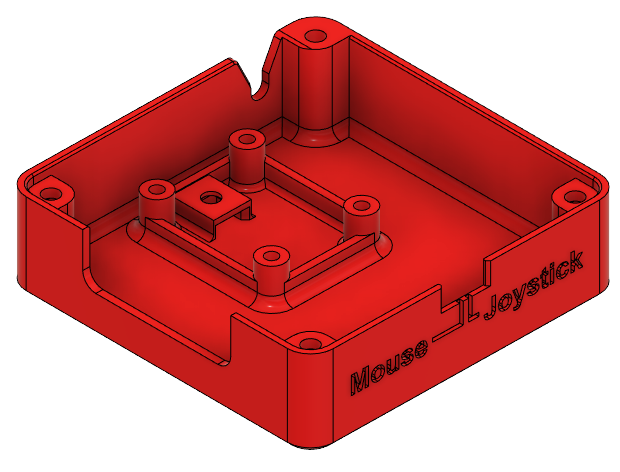
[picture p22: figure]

Lastly, there is a cut-out at the back where the USB cable exits.

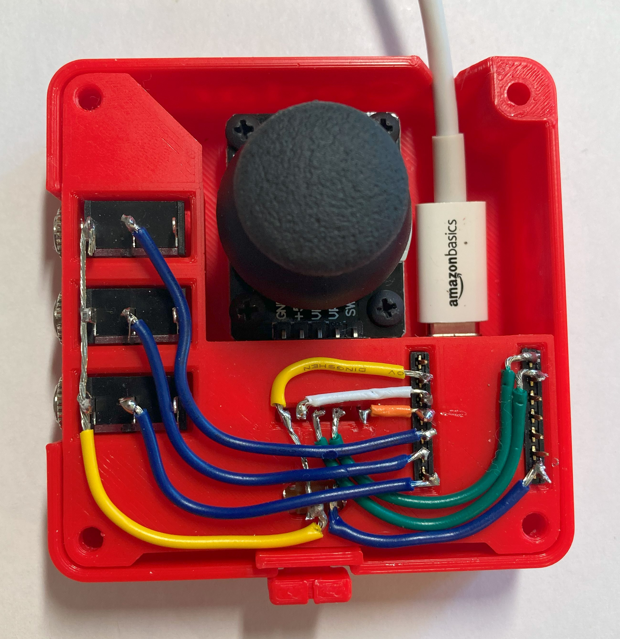
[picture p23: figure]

#### Enclosure Top

For the top of the enclosure, there is a hole for the joystick to go through, an arrow showing the ‘up” direction on the joystick, labels for the switch jacks, and alignment tabs for attaching the top and bottom together. There are also an insert for the cable hole, and four screw holes in the corners. The diameter of these screw holes is 2.68 mm for size 4 self threading sheet metal screws.

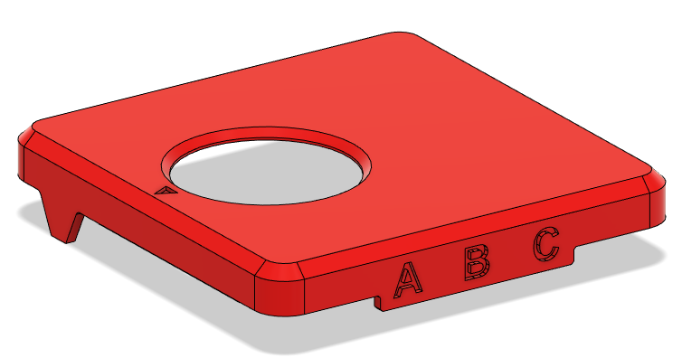
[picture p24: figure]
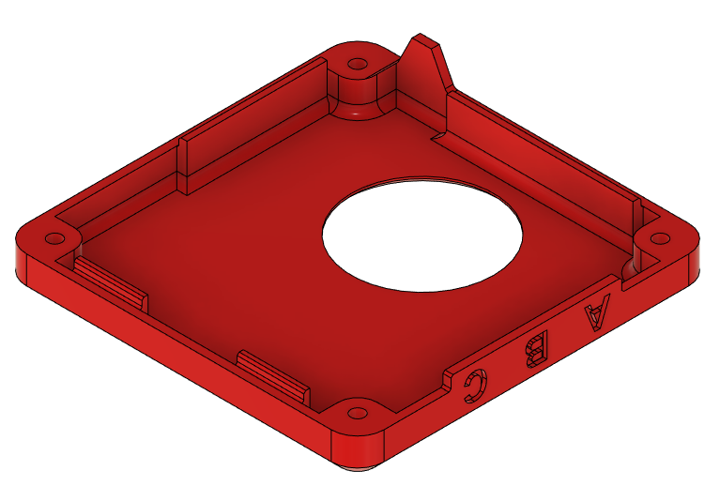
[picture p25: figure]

### Firmware Design

The overall function of the code is mentioned above, with mouse mode and joystick mode included in one firmware and the mode being set by a slide switch. The switch outputs of three switches and the joystick pressdown button are represented in the following table:

Switch | Mouse | Joystick
| | PC | XAC (left) | XAC (right)
A | Left click | Button 1 | X1 | View
B | Middle click (scroll) | Button 2 | X2 | Menu
C | Right click | Button 3 | Left stick (left press) | Right stick (right press)
Joystick push down | Left click | Button 4 | Left bumper | Right bumper

There are also some variables at the start of the code that can be changed to customize the joystick functionality for the user, these include:

- Deadzone level (JOYSTICK_DEFAULT_DEADZONE_LEVEL)
- Mouse movement speed (MOUSE_MAX_XY)

## Testing

## Opportunities for Improvement (OFI)

- Add rounded corners to 3DP Circuit Board
- Reduce different types of fasteners
  - #4 self-tapping screws
  - M3 mounting screws
- Mounting interface fastener sizing
  - availability of sizes
- Mounting interface hole spacing
  - Is there a standard/common mounting hole spacing what could be used?
- Cable strain relief
- Mono jack mounting
  - Add material so it is not just reliant on the panel mount nut
    - Add some underneath to prevent it from going “through” 3D PCB
    - Maybe add snap fit when pushing the mono jack into place
- Gap between joystick topper and enclosure
  - Reduce this or add something between them so things don’t fall in
- Components:
  - Joystick unit in single quantity
  - Joystick unit supplier that is reliable and consistent product
- Wiring
  - Difficult to wire, requires precision and time
    - Consider a PCB for this? Especially for build events?
    - Consider wire channels, similar to Lynx?

Design choices to ask about during user testing, potential OFIs

- Placement of mono jacks, slide switch, and USB-C exit
- Position of joystick in enclosure, would users prefer it is centered front to back?

© 2026 by Neil Squire This work is licensed under the CC BY SA 4.0 License: http://creativecommons.org/licenses/by-sa/4.0 Files available at https://github.com/makersmakingchange/Cedar-Mini-Joystick Page 1 of 1

V1.0 | SEPTEMBER 2025 Cedar USB Joystick Design Rationale

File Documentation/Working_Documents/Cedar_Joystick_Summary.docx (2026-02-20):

# Overview

The Device Summary is intended to be a detailed summary of the device, product and maker information for the Cedar Mini USB Joystick, making it easier to add to the Makers Making Change website. It is intended for anyone who will view the device listing.

A photo of a fully assembled Cedar USB Joystick.

# Product Information

## Product Name

Cedar Mini USB Joystick

## Device Category

Mark any relevant categories with an “X”:

| Adapted Toys
| Aids for Daily Living (ADL)
| Assistive Switches
| Communication Aids (AAC)
X | Computer Access
| Environmental Controls
X | Gaming
| Keyguard
| Kits
| LipSyncs
| Mounting
| Recreation and Leisure
| Seating and Positioning
| Switch Interfaces
| Writing Aids

## User Value Statement

A USB joystick with a small range of motion and additional switch ports that has a switch to toggle between mouse and gamepad output.

## Designer

Makers Making Change

# Device Information

## Overview

The Cedar is a small USB joystick that can act as a HID Mouse or an HID Gamepad. It connects directly to a compatible device via the integrated USB cable. The mode can be changed by sliding a switch on the enclosure. The joystick can be pressed down as an input, and up to 3 assistive switches can be connected using the 3.5 mm input jacks.

The PS2-style game controller thumbstick joystick has a range of motion of ±30° and requires approximately 75 grams-force to fully deflect. A range of toppers are available for this joystick, including a set of toppers created by AbleGamers Charity (https://www.printables.com/model/501869-analog-thumbstick-topper-collection).

In Joystick mode, it is compatible with the Xbox Adaptive Controller.

The Cedar Mini USB Joystick is the USB version of the Spruce Mini Joystick (https://www.makersmakingchange.com/product/spruce-mini-joystick/01tJR000000EHqbYAG). The Spruce Mini Joystick uses the same thumbstick component, but instead of USB output it has a TRRS cable for the joystick and a mono cable for the integrated joystick button.

Compatibility

Mouse mode – compatible with PC, most Android phones and tablets, and Apple phones and tablets with iOS13 and iPadOS.

Joystick mode – compatible with PC (direct or gaming with Steam), most Android phones and tablets, and Apple phones and tablets with iOS13 and iPadOS, and with Xbox Adaptive Controller (XAC). Through the XAC it is compatible with PC and Xbox directly or can be used with other gaming consoles with adapters.

## Disability Type

Select one or more disability types and mark with an “X”:

X | Agility / Dexterity
| Arthritis
| Cognitive
| Hearing
| Mobility
| Pain
X | SCI
| Vision
| Other

## Disability Type Description

This device is intended for users with a small range of motion that need an external joystick for adaptive gaming or computer access.

## How To Use

For full instructions please refer to the User Guide.

Usage

Using the Joystick in Mouse Mode:

1. Move the slide switch to the left for Mouse Mode, as indicated on the housing.
2. Plug in assistive switches to the switch jacks. The default switch mapping is stated below.
3. Plug the joystick into the device you wish to use it with.
4. Orient the joystick so the arrow on top is facing away from the user and the cable is exiting the enclosure away from the user.
5. Move the joystick to move the mouse, use the switches for the functions listed below.

Using the Joystick in Joystick Mode:

1. Move the slide switch to the right for Joystick Mode, as indicated on the housing.
2. If desired, plug in assistive switches to the switch jacks. The default switch mapping is stated below.
3. Plug the joystick into the device you wish to use it with.
4. Orient the joystick so the arrow on top is facing away from the user and the cable is exiting the enclosure away from the user.
5. Move the joystick to move the mouse, use the switches for the functions listed above.
6. Depending on what device you are using the joystick with, if you are using switches plugged into the jacks you will most likely want to remap them. This can be done in your system’s settings.

## Estimated Cost

The estimated material cost of the device for a single build:

| $0 - $10
| $11 - $25
| $26 - $50
X | $51 - $100
| $101 - $250
| $250+

## Attribution

Designed by Neil Squire Society / Makers Making Change

Contributors:

- Josie Versloot
- Milad Hajihassan
- Emily Schwitz
- Tyler Fentie
- Jake McIvor

# Maker Information

## Project Skills

Mark the required project skills with an “X”:

X | 3D Printing
| Custom PCB
| Electronics
| Laser Cutting
| Mechanics
X | Software
X | Soldering
| Woodworking
| Other

## Skills Description

## This is an advanced build requiring electronics, mechanics, 3D printing and using the Arduino IDE.

## Tools Needed

X | 3D Printer
X | Common Hand Tools
| Common Power Tools
| Laser Cutter
X | Soldering Iron
| Specialized Tooling

## Print time (hrs)

4

## Assembly time (hrs)

3

## Build Instructions

This is an advanced build that requires routing and soldering wires using a 3D printed circuit board.

## For full instructions, please refer to the Maker Guide available via the Project Link or Download Button.

## Download Link

https://github.com/makersmakingchange/Cedar-Mini-USB-Joystick/archive/refs/heads/main.zip

## Project Link

https://github.com/makersmakingchange/Cedar-Mini-USB-Joystick

# License

## License

Hardware: CERN 2.0 Weakly Reciprocal license

Software:

Documentation: CC BY-SA

© 2026 by Neil Squire This work is licensed under the CC BY SA 4.0 License: http://creativecommons.org/licenses/by-sa/4.0 Files available at https://github.com/makersmakingchange/Cedar-Mini-Joystick Page 1 of 2

V1.0 | August 2025 Cedar USB Joystick Summary

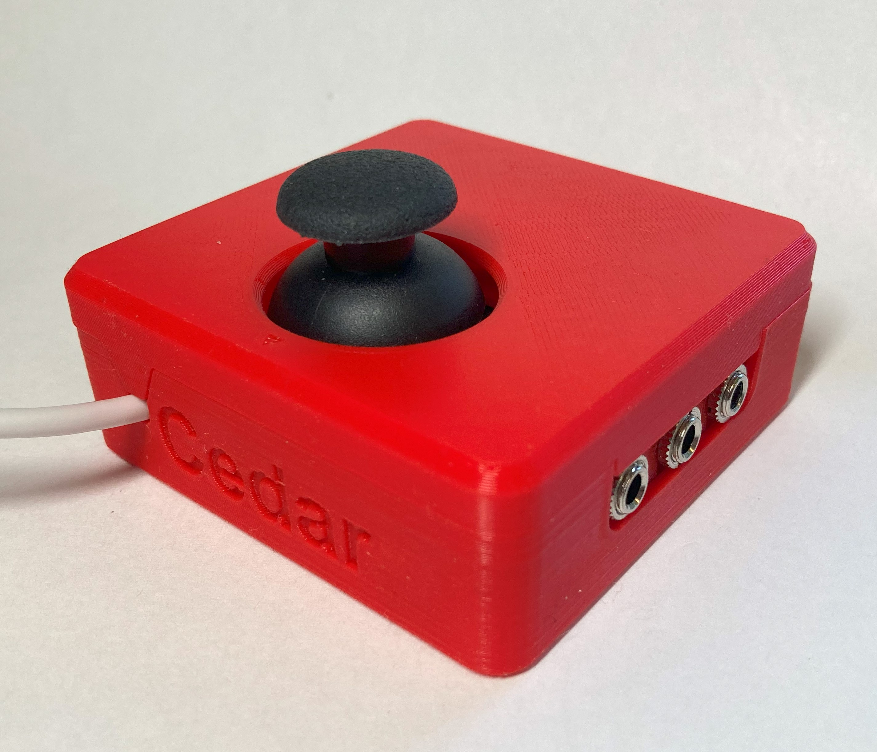
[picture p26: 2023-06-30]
Photos/Cedar_Mini_Joystick_back.jpg

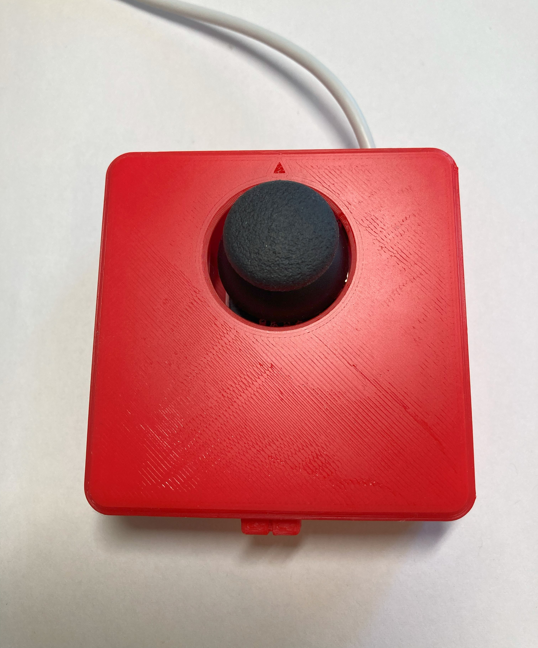
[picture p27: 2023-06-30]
Photos/Cedar_Mini_Joystick_top.jpg

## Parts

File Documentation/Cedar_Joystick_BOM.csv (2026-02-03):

Device: | Cedar Mini USB Joystick
Version: | V1.0
Last Updated: | 2025-09-15
 |  |  |  |  |  |  |  | Total filament (g) |  | Unit Cost | Total Estimated Cost | Build Cost
 |  |  |  |  |  |  |  | 42.3 |  | $42.79 | $62.58
ID | Commercial Parts |  |  |  |  |  |  |  |  | $41.73 | $61.52
 | Part | Description |  | Manufacturer | Supplier | QTY / Device | QTY / PKG | PKGs | $/ PKG | $ / Device | Total Estimated Cost |  | Link
 | Joystick (PS2) | Electrical |  | Wishiot | Amazon | 1 | 10 | 1 | 21.99 | $2.20 | $21.99 |  | https://www.amazon.ca/dp/B089VXPHDH?_encoding=UTF8&psc=1&ref_=cm_sw_r_cp_ud_dp_GGTEDME4PM2P27SG86P7
 | USB-C cable, 6 ft (can buy this locally) | Electrical |  | Cvilux USA | DigiKey | 1 | 1 | 1 | 3.43 | $3.43 | $3.43 |  | https://www.digikey.ca/en/products/detail/cvilux-usa/DH-20M50053/13177348
 | Adafruit QT Py SAMD21 | Electrical |  | Adafruit Industries LLC | DigiKey | 1 | 1 | 1 | 10.93 | $10.93 | $10.93 |  | https://www.digikey.ca/en/products/detail/adafruit-industries-llc/4600/13543375
 | 3.5 mm mono jack, panel mount | Electrical |  | Same Sky | DigiKey | 3 | 1 | 3 | 2.19 | $6.57 | $6.57 |  | https://www.digikey.ca/en/products/detail/cui-devices/MJ-3502/281321
 | Slide switch, right angle | Electrical |  | C&K | DigiKey | 1 | 1 | 1 | 0.95 | $0.95 | $0.95 |  | https://www.digikey.ca/en/products/detail/c-k/OS102011MA1QS1/1981431
 | Right angle female header, 5 position | Electrical |  | Sullins Connector Solutions | DigiKey | 1 | 1 | 1 | 0.76 | $0.76 | $0.76 |  | https://www.digikey.ca/en/products/detail/sullins-connector-solutions/PPTC051LGBN-RC/775899
 | Female header, 7 position, single row, 0.100" | Electrical |  | Sullins Connector Solutions | DigiKey | 2 | 1 | 2 | 0.68 | $1.36 | $1.36 |  | https://www.digikey.ca/en/products/detail/sullins-connector-solutions/PPTC071LFBN-RC/810146
 | Sheet Metal Screw, #4, 3/8″ Length (if building more than one, link below) | Mechanical |  | Serpac | DigiKey | 8 | 1 | 8 | 0.61 | $4.88 | $4.88 |  | https://www.digikey.ca/en/products/detail/serpac/6005/307599
 | Wire, 24 AWG, solid core, 1 foot, white | Electrical |  | CNC Tech | DigiKey | 1 | 1 | 1 | 0.73 | $0.73 | $0.73 |  | https://www.digikey.ca/en/products/detail/cnc-tech/1007-24-1-2000-002-1-TD/17799208
 | Wire, 24 AWG, solid core, 1 foot, black | Electrical |  | CNC Tech | DigiKey | 1 | 1 | 1 | 0.73 | $0.73 | $0.73 |  | https://www.digikey.ca/en/products/detail/cnc-tech/1007-24-1-2000-001-1-TD/17799235
 | Wire, 24 AWG, solid core, 1 foot, green | Electrical |  | CNC Tech | DigiKey | 1 | 1 | 1 | 0.73 | $0.73 | $0.73 |  | https://www.digikey.ca/en/products/detail/cnc-tech/1007-24-1-2000-007-1-TD/17799170
 | Cable Tie, 4 in. | Mechanical |  | TE Connectivity AMP Connectors | DigiKey | 1 | 1 | 1 | 0.16 | $0.16 | $0.16 |  | https://www.digikey.ca/en/products/detail/te-connectivity/2-604771-9/2259327
 | Hex Nut, M3 | Mechanical |  | Keystone Electronics | DigiKey | 2 | 1 | 2 | 0.15 | $0.30 | $0.30 |  | https://www.digikey.ca/en/products/detail/keystone-electronics/4708/4499301
 | Machine Screw, M3, Pan Head, 12mm (Optional for mount) | Mechanical |  | APM Hexseal | DigiKey | 0 | 1 | 0 | 0.98 | $- | $- |  | https://www.digikey.ca/en/products/detail/apm-hexseal/RM3X12MM-2701/2063201
 | Tee nut, 1/4-20 UNC, 5/16 in length (Optional for mount) | Mechanical |  | Paulin | Home Depot | 0 | 1 | 0 | 0.55 | $- | $- |  | https://www.homedepot.ca/product/paulin-1-4-inch-20-tee-nuts-4-prong-5-16-inch-barrel-length/1000129429
 | Digikey shipping (if spending less than $100) | Shipping |  |  |  | 1 | 1 | 1 | 8 | $8.00 | $8.00
 | 3D Printed Parts |  |  |  |  |  |  | 42.3 |  | $1.06 | $1.06
 | Part | Description | Filament Type | Filament | Color | QTY / Device | Mass (g) / Part | Total Mass | $ / kg | $ / Device | Total Estimated Cost |  | Link
 | Enclosure bottom |  | PLA |  | Any | 1 | 20.2 | 20.2 | $25.00 | $0.51 | $0.51
 | Enclosure top |  | PLA |  | Any | 1 | 11.9 | 11.9 | $25.00 | $0.30 | $0.30
 | 3D PCB |  | PLA |  | Any | 1 | 8 | 8.0 | $25.00 | $0.20 | $0.20
 | Slide switch |  | PLA |  | Any | 1 | 0.6 | 0.6 | $25.00 | $0.02 | $0.02
 | RAM or 1/4-20 Mounting Adapter (Optional) |  | PLA |  | Any | 1 | 1.6 | 1.6 | $26.00 | $0.04 | $0.04
 | Custom PCB |  |  |  |  |  |  |  |  | $- | $-
 | Part | Description |  | Manufacturer | Supplier | QTY / Device | QTY / PKG | PKGs | $/ PKG | $ / Device | Total Estimated Cost |  | Link
 | <None>
 | Tools
 | Tool | Description |  | Manufacturer | Supplier |  |  |  |  |  |  |  | Link
 | Flush cutters
 | Wire strippers
 | Soldering iron
 | Philips head screw driver
 | Alternatives
 | Part | Description |  | Manufacturer | Supplier | QTY / Device | QTY / PKG | PKGs | $/ PKG | $ / Device | Total Estimated Cost |  | Link
 | #4 Metal Screw, 3/8″ Length, 100 pack | Electrical |  | Small Parts | Amazon | 8 | 100 | 1 | 12.41 | $0.99 | $12.41 |  | https://a.co/d/523bJeL
 | USB-C cable, 3 feet | Electrical |  | Amazon | Amazon | 1 | 1 | 1 | 8.99 | $8.99 | $8.99 |  | https://a.co/d/97Y71JT
 | USB-C cable, 6 feet, 2 pack | Electrical |  | Wcakby | Amazon | 1 | 2 | 1 | 10.99 | $5.50 | $10.99 |  | https://a.co/d/6UE2og9
 | USB-C cable, 6 feet, 5 pack | Electrical |  | CLEEFUN | Amazon | 1 | 5 | 1 | 15.99 | $3.20 | $15.99 |  | https://a.co/d/b3qG7jC
 | Cable Tie | Mechanical |  | Heyco Products Corporation | DigiKey | 1 | 1 | 1 | 0.15 | $0.15 | $0.15 |  | https://www.digikey.ca/en/products/detail/heyco-products-corporation/13123B/15791902
 | Wire, 22 AWG, Solid Core, Multiple Color Pack | Electrical |  | Adafruit | Adafruit |  |  |  |  |  |  |  | https://www.adafruit.com/product/1311
 |  |  |  |  |  |  |  |  |  |  |  |  | https://www.digikey.ca/en/products/detail/adafruit-industries-llc/1311/6198255

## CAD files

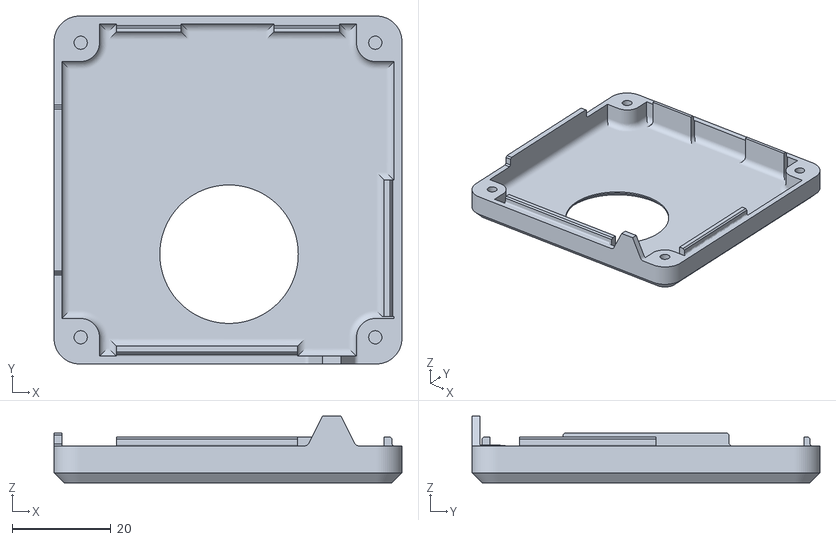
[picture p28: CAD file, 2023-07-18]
Build_Files/3D_Printing_Files/Enclosure_top.stl
70.4 x 70.4 x 13.5

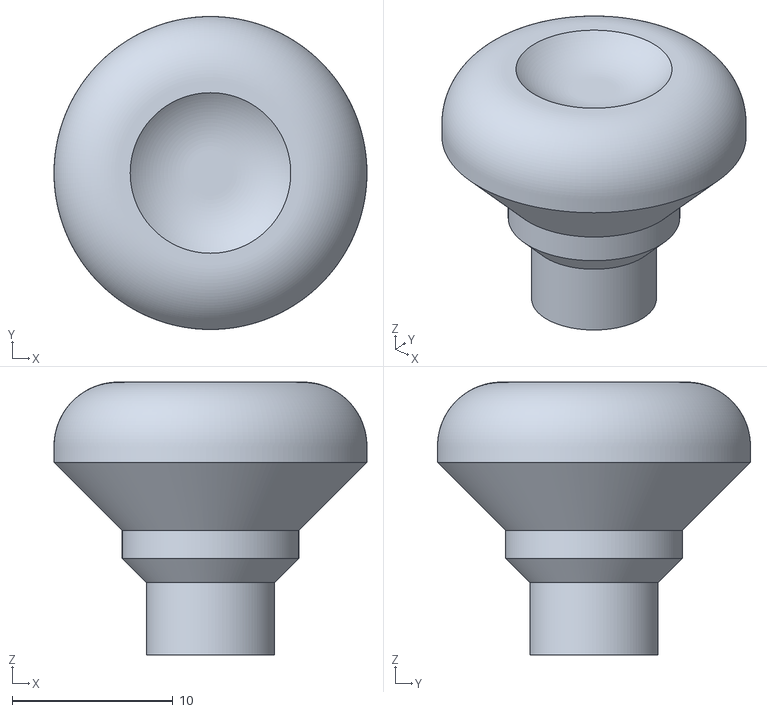
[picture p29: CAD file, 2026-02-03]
Build_Files/3D_Printing_Files/Toppers/Additional Toppers/standard.stl
19.5 x 19.5 x 17.0

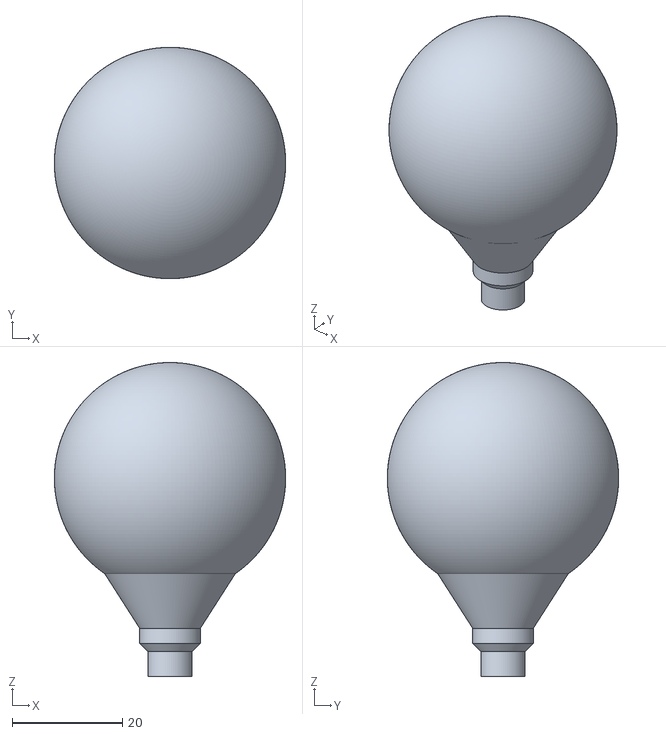
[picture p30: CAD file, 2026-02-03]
Build_Files/3D_Printing_Files/Toppers/Ball_Topper.stl
42.0 x 42.0 x 57.0

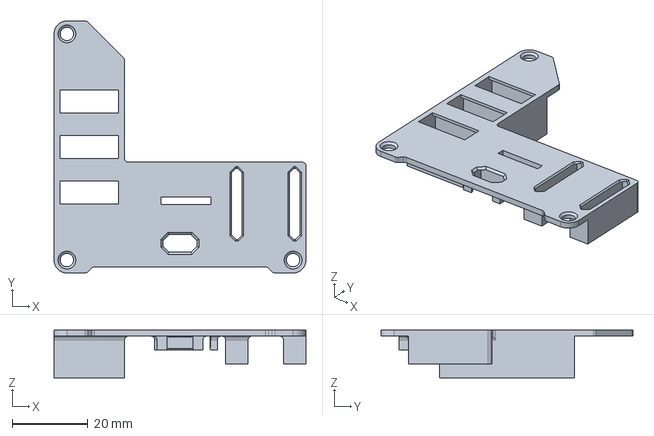
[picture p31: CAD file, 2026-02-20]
Design_Files/CAD_Design_Files/Step/3D_PCB.step
66.4 x 66.4 x 12.6 mm

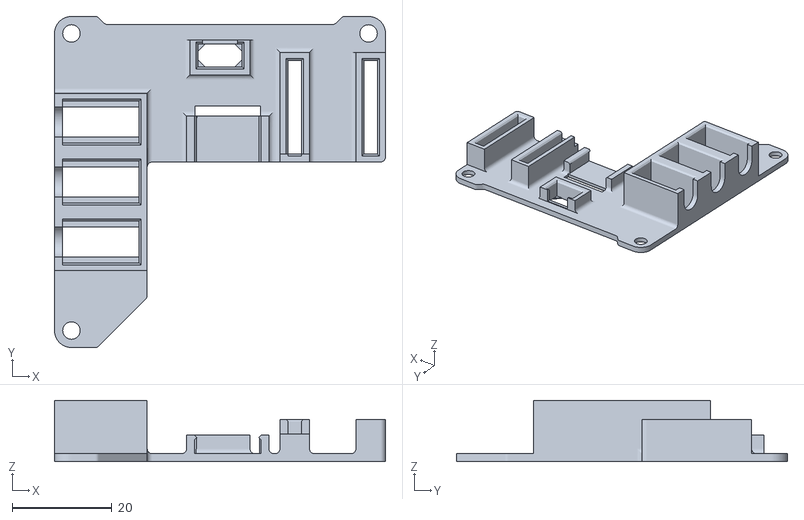
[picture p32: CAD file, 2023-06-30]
Build_Files/3D_Printing_Files/3D_PCB.stl
66.4 x 66.4 x 12.3

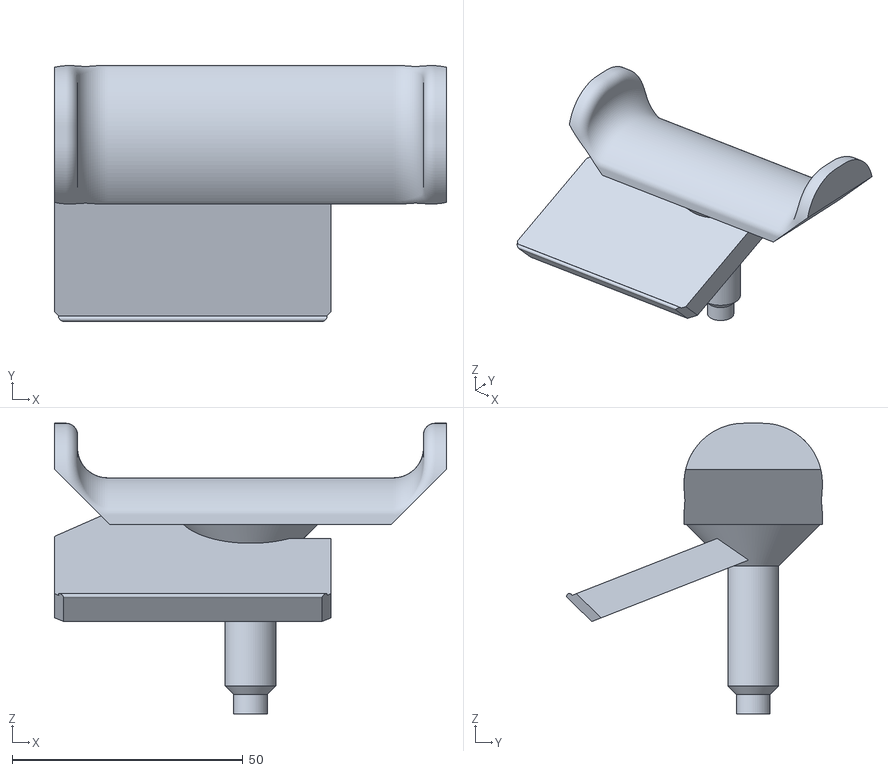
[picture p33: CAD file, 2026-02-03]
Build_Files/3D_Printing_Files/Toppers/Additional Toppers/fps.stl
85.0 x 55.5 x 63.0

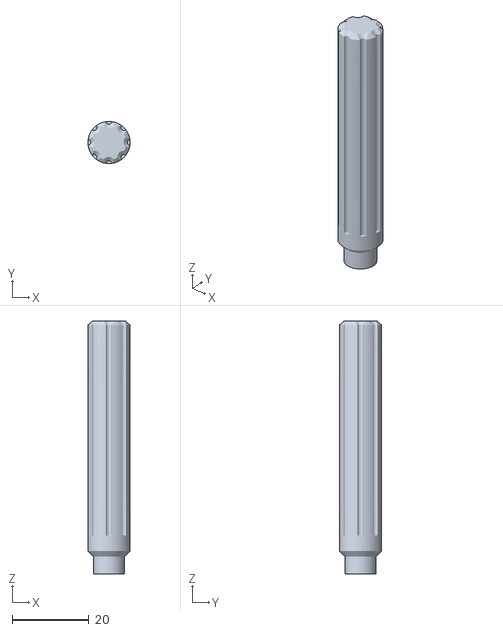
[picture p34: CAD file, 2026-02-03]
Build_Files/3D_Printing_Files/Toppers/Stick_Topper.stl
11.0 x 11.0 x 66.0

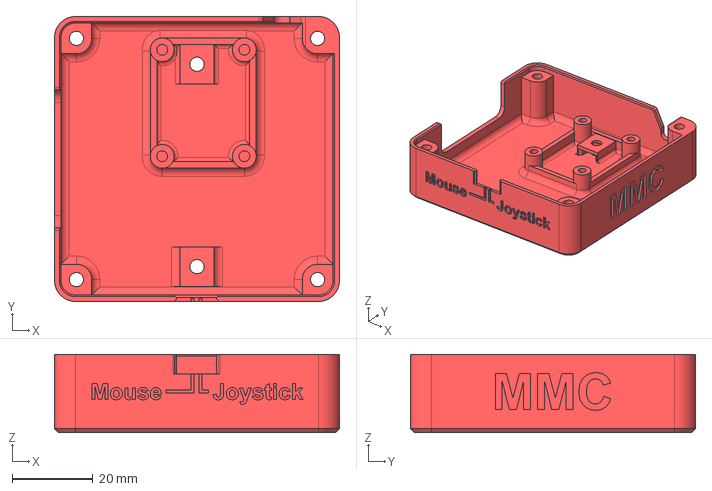
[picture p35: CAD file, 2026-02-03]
Design_Files/CAD_Design_Files/Step/Enclosure_bottom.step
70.4 x 70.4 x 19.4 mm

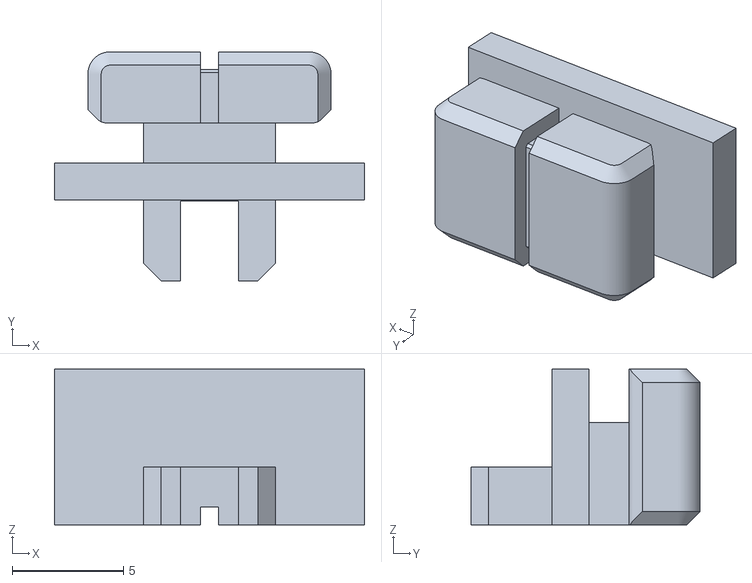
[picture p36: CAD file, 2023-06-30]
Build_Files/3D_Printing_Files/Switch_Slide.stl
13.9 x 10.3 x 7.00

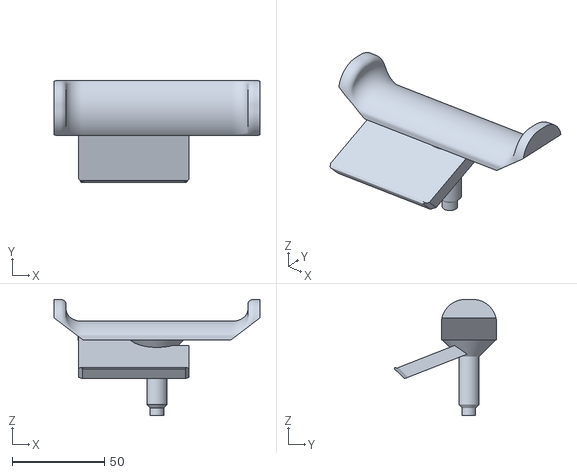
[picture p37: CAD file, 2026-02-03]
Build_Files/3D_Printing_Files/Toppers/Additional Toppers/fps-super-wide.stl
111.7 x 55.5 x 63.0

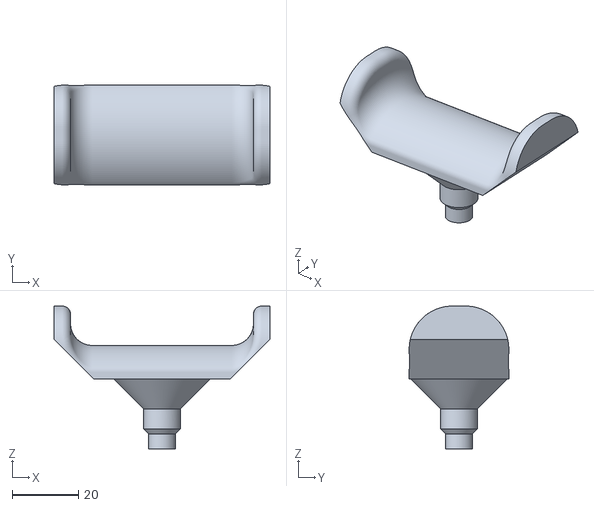
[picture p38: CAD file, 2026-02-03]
Build_Files/3D_Printing_Files/Toppers/Small_Goalpost_Topper.stl
65.0 x 30.0 x 43.0

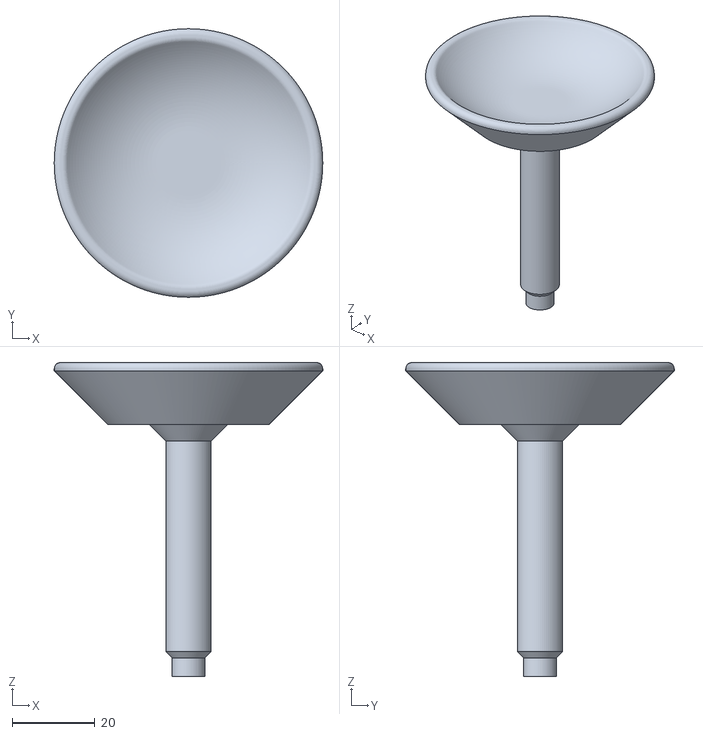
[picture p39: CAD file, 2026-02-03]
Build_Files/3D_Printing_Files/Toppers/Additional Toppers/chin cup.stl
65.0 x 65.0 x 76.0

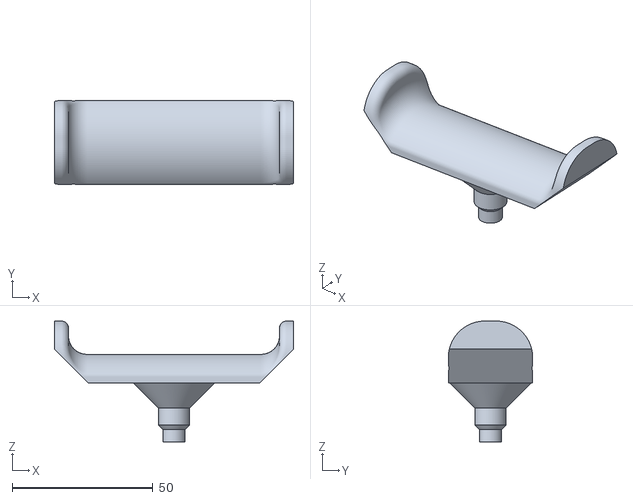
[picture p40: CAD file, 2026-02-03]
Build_Files/3D_Printing_Files/Toppers/Large_Goalpost_Topper.stl
85.0 x 30.0 x 43.0

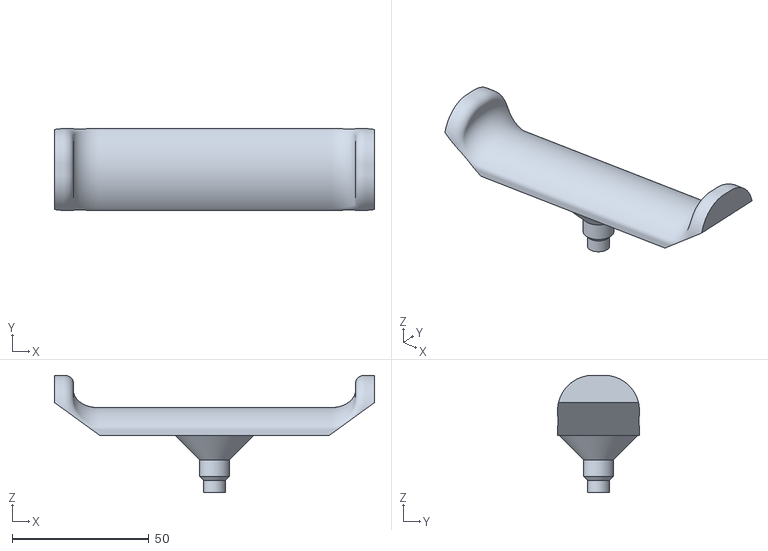
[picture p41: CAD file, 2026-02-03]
Build_Files/3D_Printing_Files/Toppers/Additional Toppers/thumbstick-super-wide.stl
117.1 x 30.0 x 43.0

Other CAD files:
Design_Files/CAD_Design_Files/Step/Switch_Slide v5.step
Build_Files/3D_Printing_Files/Enclosure_bottom.stl
Design_Files/CAD_Design_Files/Step/Enclosure_top.step
Build_Files/3D_Printing_Files/Toppers/Concave_Topper.stl
Build_Files/3D_Printing_Files/Toppers/Additional Toppers/low-profile-dome-for-ps5.stl
Build_Files/3D_Printing_Files/Toppers/Convex_Topper.stl
Design_Files/CAD_Design_Files/Fusion/3D_PCB.f3d
Design_Files/CAD_Design_Files/Fusion/Enclosure_bottom.f3d
Design_Files/CAD_Design_Files/Fusion/Enclosure_top.f3d
Design_Files/CAD_Design_Files/Fusion/Switch_Slide v5.f3d

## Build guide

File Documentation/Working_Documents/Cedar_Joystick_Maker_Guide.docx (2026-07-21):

# Overview

This document contains the necessary information to build the Cedar USB Joystick. This includes a Customization Guide, 3D Printing Guide, Assembly Guide, and instructions to test the finished joystick.

A photo of an assembled Cedar USB Joystick

# Maker Checklist

This list provides an overview of the steps required to build and deliver the device.

## Maker To Do List

- Read through the Maker Guide to become familiar with required components, tools, supplies, and safety gear and overall assembly steps.
- Talk to User about customization options (e.g., colour, any special requests, etc.)
- Ask the user if they would like any joystick toppers.
- Ask the user if they would like a specific mounting solution.
  - Tabletop
    - Hook and Loop Fasteners
    - Non slip material
  - Camera Mount Adapter
  - RAM Mount Adapter
- Order hardware components
- Gather tools, supplies, and safety equipment.
- Print the 3D printed components.
- Assemble the device
- Test device
- Print “User Guide”

## Items to Give to User

- Assembled, tested joystick
- Any joystick toppers if requested
- Any mount adapters if requested
- “User Guide”

# Tool List

## Tools / Equipment

Tool ID | Description | Required / Recommended | Notes
T01 | Flush Cutters | Required
T02 | Wire Strippers | Required
T03 | Soldering Iron | Required
T04 | Philips Head Screwdriver | Required
T05 | Computer with USB port | Required | Must have Arduino IDE or the ability to install it

## Supplies

Supplies ID | Description | Quantity | | Notes
S01 | Solder | 5 grams

## Personal Protective Equipment (PPE)

PPE ID | Description | Notes
P01 | Safety Goggles

# Customization Guide

## Joystick

The enclosure can be printed in the user’s desired colour(s). Colour swaps can be done to further customize the joystick and make the forward arrow on the top stand out more.

## Toppers

3D printed joystick toppers can be added to the joystick to better suit the user’s needs and abilities.

Any PS2 style thumbstick toppers will work here, one example is this set of toppers designed by AbleGamers[^1]. (https://www.printables.com/model/501869-analog-thumbstick-topper-collection) A copy of the AbleGamers toppers can be found in the toppers folder.

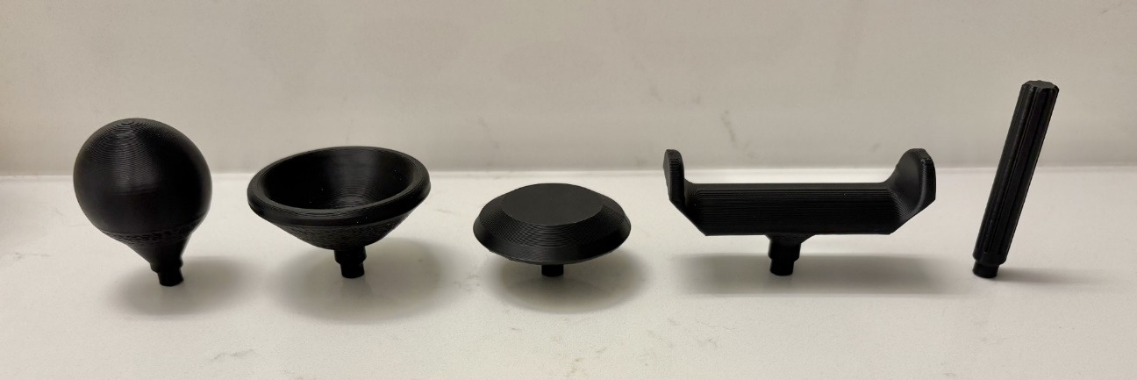
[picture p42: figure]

## Mounting

A Mounting Adapter can be added for custom mounting solutions. Current mounting options include nonslip pads, hook and loop fastener, and a ¼-20 UNC Camera Mount Adapter.

# 3D Printing Guide

## 3D Printing Summary

Metrics | Single Unit
Total Print Time (min) | 4h53m
Total Number of Components | 4
Typical Total Mass (g) | 41
Typical Number of Print Setups | 1

## 3D Printing Settings

Note that the 3D printing material should be assumed to be PLA unless otherwise noted in the table below.

Print File Name | Qty | Total Print Time (hr:min) | Mass (g) | Infill (%) | Support (Y/N) | Layer Height/ Nozzle Diameter(mm) | Notes
Enclosure_bottom.stl | 1 | 2:29 | 20 | 20 | N | 0.2/0.4 | Print in orientation given in STL
Enclosure_top.stl | 1 | 1:19 | 12 | 20 | N | 0.2/0.4 | Print in orientation given in STL
3D_PCB.stl | 1 | 0:57 | 8 | 20 | N | 0.2/0.4 | Print in orientation given in STL
Slide_switch.stl | 1 | 0:08 | 1 | 20 | N | 0.2/0.4 | Print in orientation given in STL

## Post-Processing

Inspect the 3D printed parts for any printing defects, sharp edges, or burrs. Sharp edges and burrs can be removed with sanding or deburring tools.

## Examples of Quality Prints

Compare your 3D prints to the images here. If there are significant differences, you may need to reprint the part.

Joystick Enclosure
Enclosure_bottom.stl | Enclosure_top.stl | 3D_PCB.stl
Slide_switch.stl

# Assembly Guide

## Part A: Joystick Assembly

### Required Components

1 | Joystick Component | QTY 1 | 2 | USB-C cable | QTY 1 | 3 | Adafruit QT Py SAMD21 board | QTY 1
4 | 3.5 mm mono jack, panel mount | QTY 3 | 5 | Slide Switch | QTY 1 | 6 | Right angle 5 pin female header | QTY 1
7 | Female header, 7 pin | QTY 2 | 8 | #4-3/8” Sheet metal screw, self threading | QTY 4 | 9 | 24AWG solid core wire, multiple colours | Length: 2 feet
10 | Cable Tie, 4” | QTY 1 | 11 | M3 Hex Nuts | QTY 2 | 12 | 3D Printed PCB | QTY 1

### Required Tools

- Flush Cutters
- Wire Strippers
- Soldering Iron
- Philips Head Screwdriver
- Computer with USB port and Arduino IDE (or ability to install it)

### Required Personal Protective Equipment (PPE)

- Safety Goggles

### Assembly Steps

#### Step 1: Insert Slide Switch

Press fit the slide switch into the 3D Printed PCB so top is flush with 3D print Use pliers to bend the two outer mounting legs outwards to secure the slide switch.

#### Step 2: Insert Female Headers

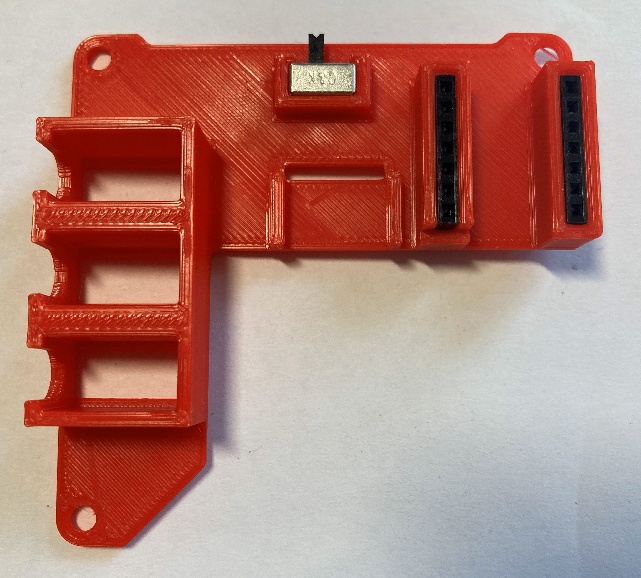
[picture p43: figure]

Insert components into 3D PCB: - Press fit both 7 pin female headers so the tops are flush with the 3D print

#### Step 3: Insert Right Angle Female Headers

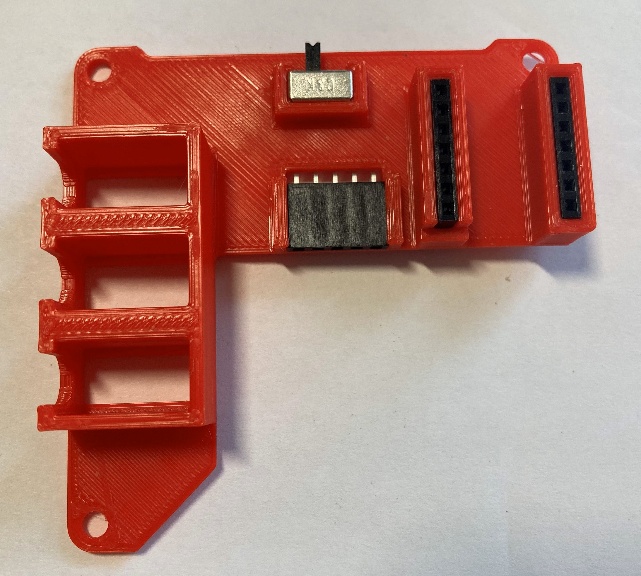
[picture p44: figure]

Insert component into 3D PCB: - Snap fit right angle 5 pin female header with pins through hole in the board

#### Step 4: Insert Mono Jacks

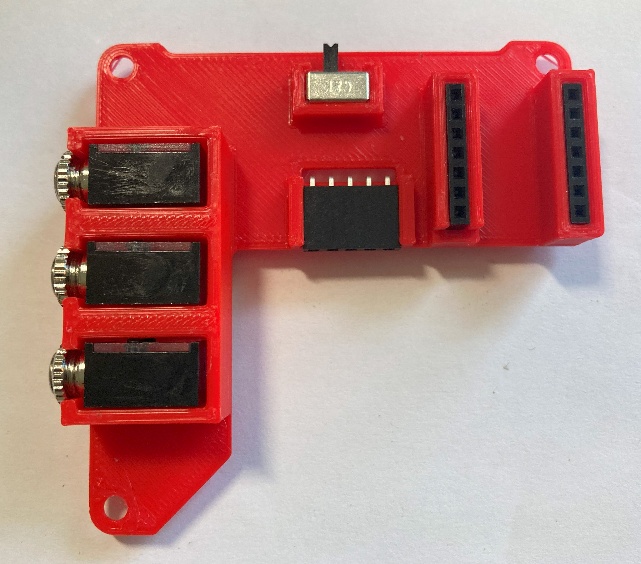
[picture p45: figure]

Insert components into 3D PCB: - Press in the mono jacks so the tops are flush with the 3D print - Install nuts on the mono jacks to secure them.

#### Wiring

Wiring the joystick will follow the diagram below and will be broken down into multiple steps.

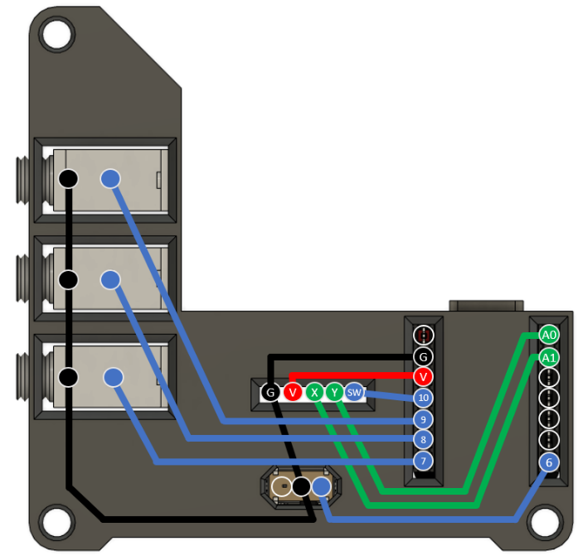
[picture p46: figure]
Wiring diagram for Cedar Mini joystick

Figure 1. Joystick Wiring Guide

#### Step 5: Flip the 3D PCB

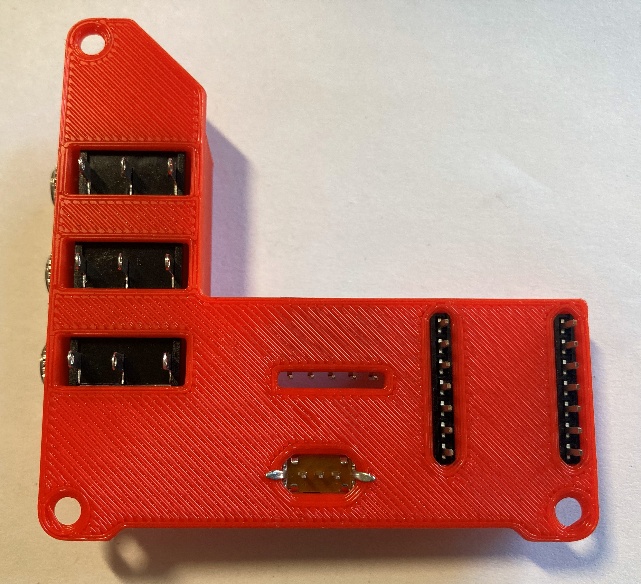
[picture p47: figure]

Flip the 3D PCB so that the pins are facing up, as shown.

#### Step 6: Prepare Wires (Colour 1)

Take one colour of wire and cut two lengths, 7 cm and 4 cm. From the longer wire, strip 1.5 cm fomr one end and 0.3 cm from the other end. From the shorter wire, strip off 3 cm from one end and 0.3 cm from the other end. | 1.5 cm 0.3 cm 4 cm 7 cm 0.3 cm 3 cm

#### Step 7: Solder First Ground Wire (Colour 1)

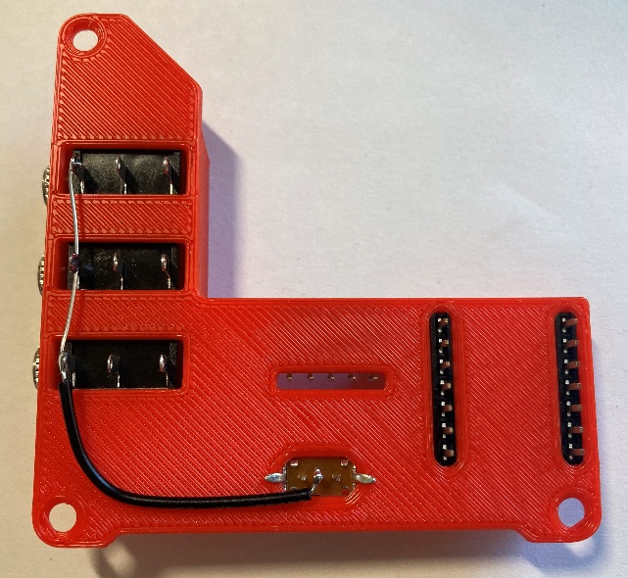
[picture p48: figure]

Take the longer wire from the previous step, bend it such that the longer stripped section is in contact with the leftmost pin of each of the 3 mono jacks, and the shorter stripped section is in contact with the middle pin on the slide switch. Solder these connections.

#### Step 8: Solder Second Ground Wire (Colour 1)

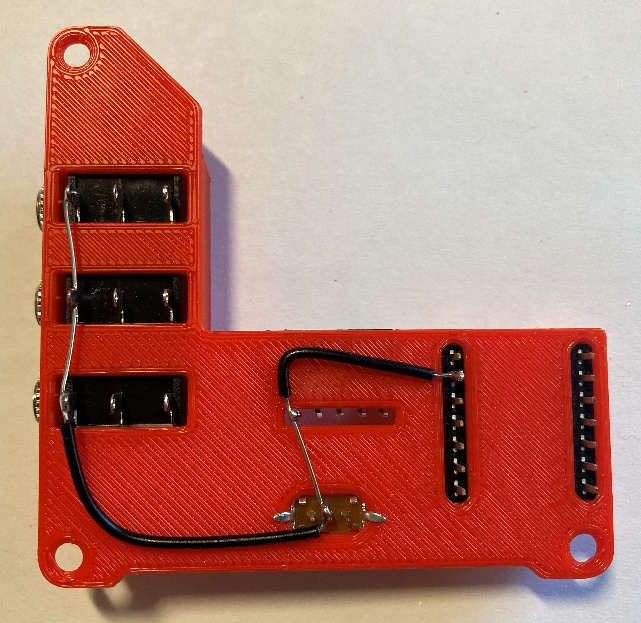
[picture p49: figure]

Take the shorter wire from Step 6, bend it such that: - The longer stripped section is in contact with the middle pin of the slide switch and the leftmost pin on the joystick header (labelled G) - The shorter stripped section is in contact with the 2nd pin from top left on QT Py header (labelled G on wiring diagram). Solder these connections.

#### Step 9: Prepare Wire (Colour 2)

Take a second colour of wire and cut a 3 cm piece. Strip off roughly 0.3 cm from each end. | 3 cm 0.3 cm 0.3 cm

#### Step 10: Solder Voltage Wire (Colour 2)

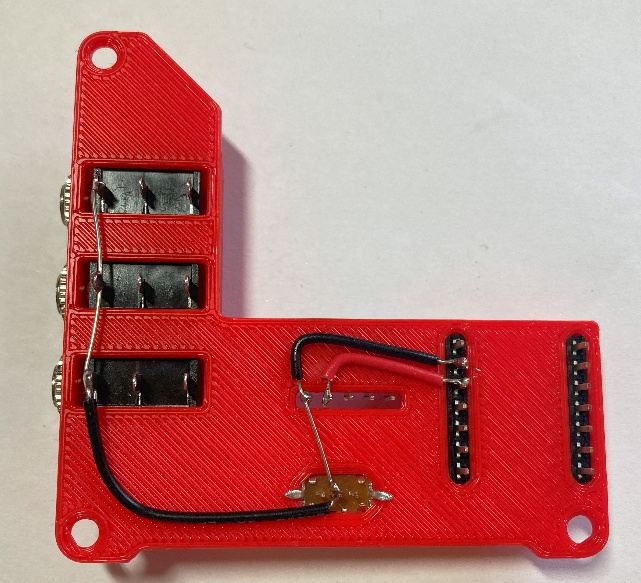
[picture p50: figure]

Take the wire (colour 2) from the previous step and bend it so it will touch: - the second pin (from the left) on the joystick header (labelled V) - the third pin from the top left on the QT Py header (3v3 pin, labelled V on wiring diagram). Solder these connections.

#### Step 11: Prepare Wires (Colour 3)

Take a third colour of wire and cut a two pieces 5 cm long each. - Strip off roughly 0.3 cm from each end of both wires. | 0.3 cm 0.3 cm 5 cm

#### Step 12: Solder Joystick Y Wire (Colour 3)

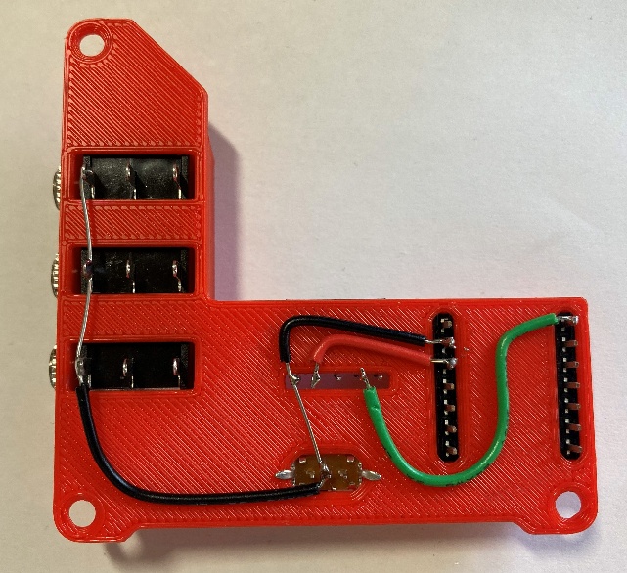
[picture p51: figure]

Take the 5 cm wire (colour 3) from the previous step and bend it so it will touch: - the fourth pin (from the left) on the joystick header (labelled Y on wiring diagram) - the first pin from the top right on the QT Py header (labelled A0 on wiring diagram). Solder these connections.

#### Step 13: Solder Joystick X Wire (Colour 3)

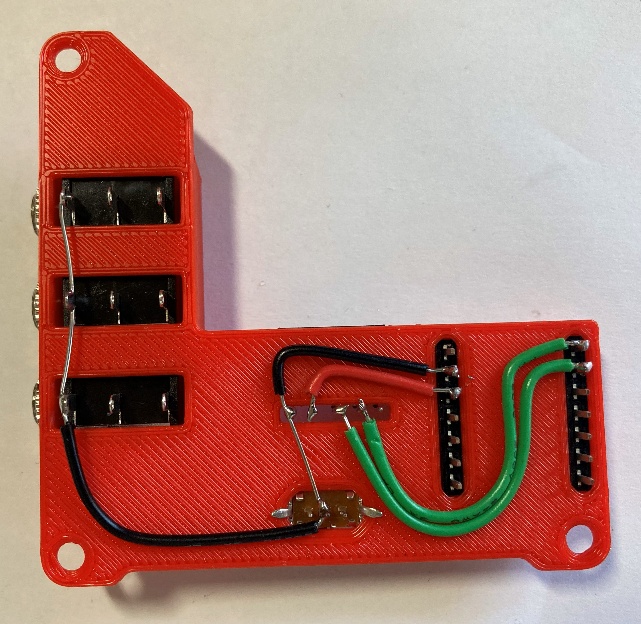
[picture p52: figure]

Take the 5 cm wire (colour 3) from the previous step and bend it so it will touch: - the third pin (from the left) on the joystick header (labelled X on wiring diagram) - the second pin from the top right on the QT Py header (labelled A1 on wiring diagram). Solder these connections.

#### Step 14: Prepare Wire (Colour 4)

Take a fourth colour of wire and cut a piece 1 cm long. Strip off roughly 0.2 cm from each end of the wire. | 0.2 cm 0.2 cm 1 cm

#### Step 15: Solder Joystick Sw Wire (Colour 4)

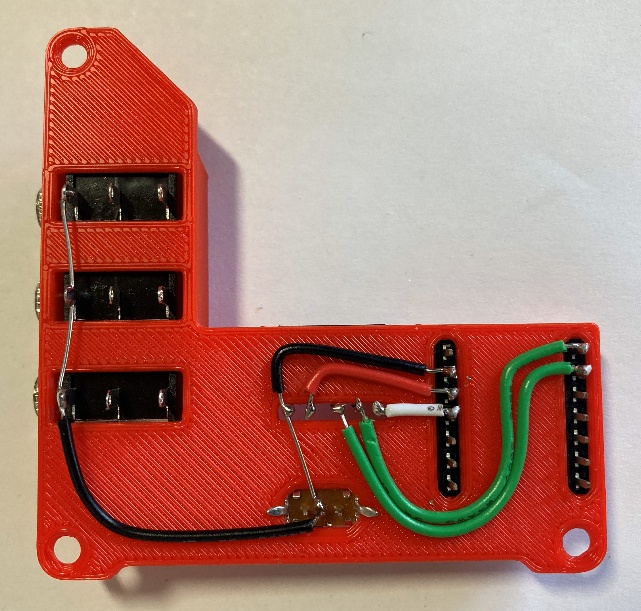
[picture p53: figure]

Take the 1 cm wire (colour 4) from the previous step and connect it so it will touch: - the fifth pin (from the left) on the joystick header (labelled Sw on wiring diagram) - the fourth pin from the top left on the QT Py header (labelled 10 on wiring diagram). Solder these connections.

#### Step 16: Prepare Wires (Colour 4)

0.2 cm

0.2 cm

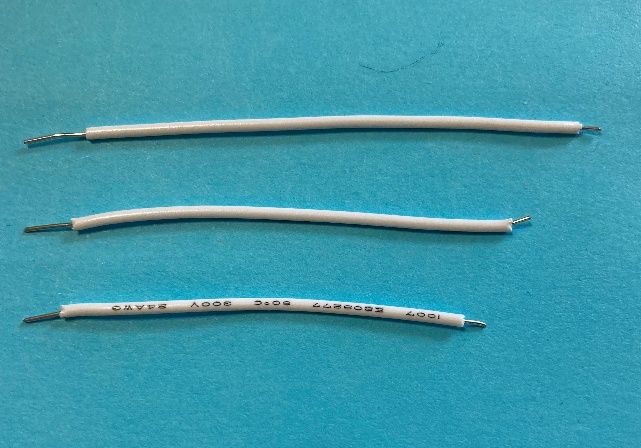
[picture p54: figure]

Take the fourth colour of wire and cut three pieces of lengths: 6.5 cm, 5.5 cm, 5.0 cm. Strip off roughly 0.2 cm from one, and 1 cm from the other end of each wire. Cut a fourth piece of wire 3.5 cm long and strip off roughly 0.2 cm from each end. | 0.2 cm 3.5 cm 1 cm 5 cm 5.5 cm 6.5 cm

#### Step 17: Solder First Switch Jack Wire (Colour 4)

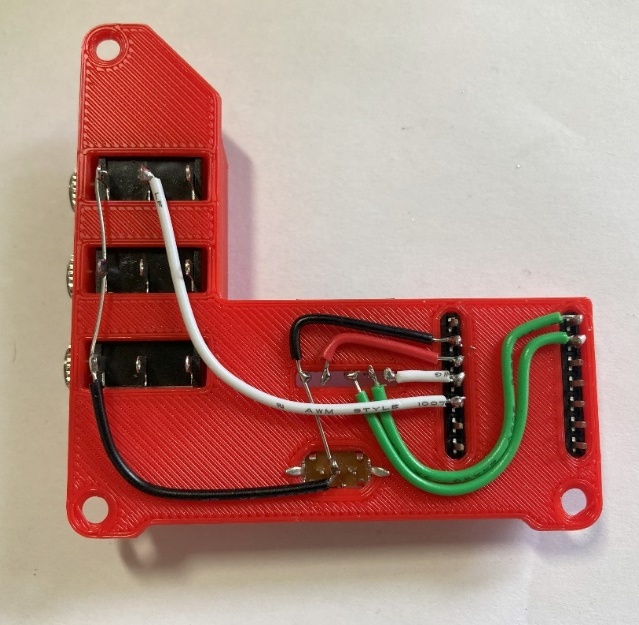
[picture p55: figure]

Take the 6.5 cm wire (colour 4) from the previous step and bend it so it will touch: - the second pin (from the left) on the top mono jack (using the side with more stripped exposed wire) - the fifth pin from the top left on the QT Py header (labelled 9 on wiring diagram). Solder these connections.

#### Step 18: Solder Second Switch Jack Wire (Colour 4)

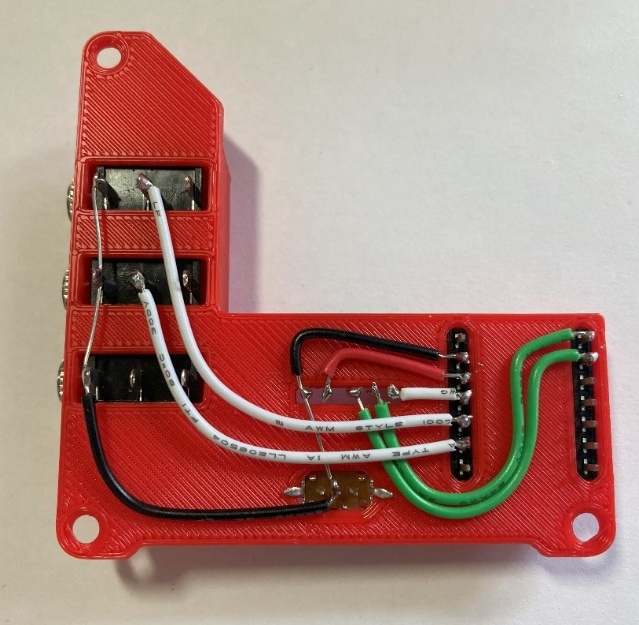
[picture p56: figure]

Take the 5.5 cm wire (colour 4) from step 16 and bend it so it will touch: - the second pin (from the left) on the middle mono jack (using the side with more stripped exposed wire) - the sixth pin from the top left on the QT Py header (labelled 8 on wiring diagram). Solder these connections.

#### Step 19: Solder Switch Slide Wire (Colour 4)

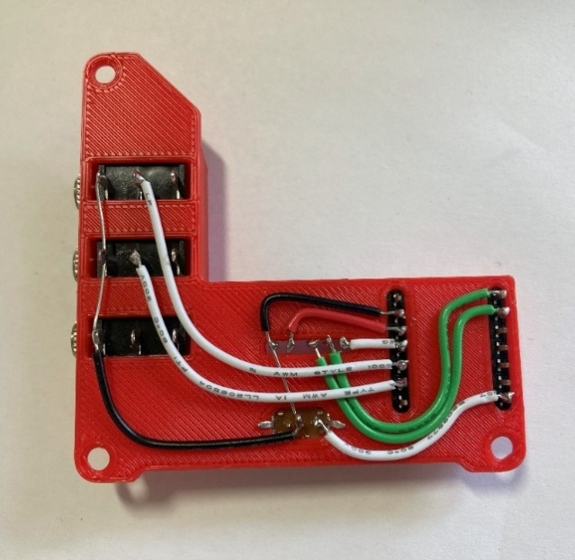
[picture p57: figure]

Take the 3.5 cm wire (colour 4) from step 16 and bend it so it will touch: - the right most pin on the slide switch - the seventh pin from the top right on the QT Py header (labelled 6 on wiring diagram). Solder these connections.

#### Step 20: Solder Third Switch Jack Wire (Colour 4)

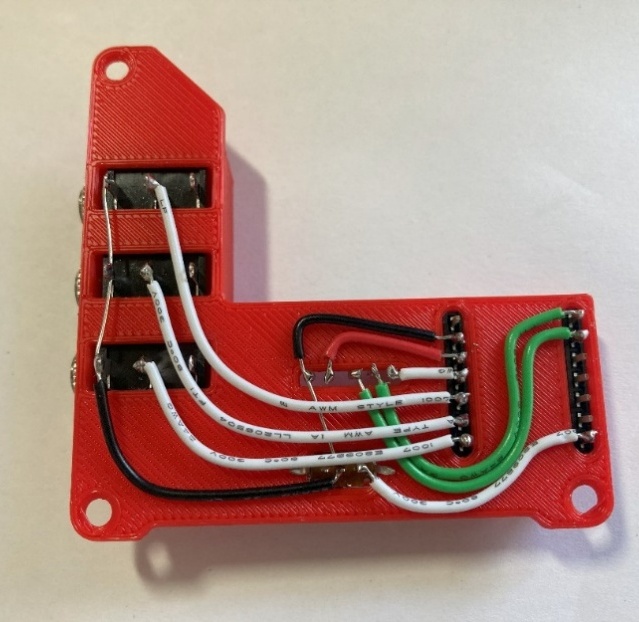
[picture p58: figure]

Take the 5 cm wire (colour 4) from step 16 and bend it so it will touch: - the second pin (from the left) on the bottom mono jack (using the side with more stripped exposed wire) - the seventh pin from the top left on the QT Py header (labelled 7 on wiring diagram). Solder these connections.

#### Step 21: Attach Microcontroller

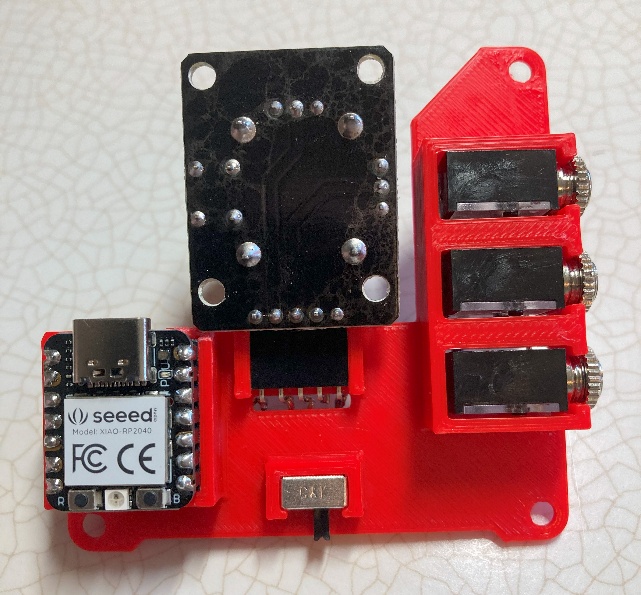
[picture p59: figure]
Top view of 3D printed circuit board with all components inserted including microcontroller and joystick.

From the male headers that came with the Adafruit QT Py SAMD21 board, break off two 7-pin pieces. Insert the long side of the 7 pin male headers into 7 pin female headers on 3D printed board. Place the Adafruit QT Py board on the male headers, ensuring the USB is facing towards the joystick. Solder the male headers to the microcontroller.

#### Step 22: Attach Joystick Unit

Insert joystick into angled headers. All components should be “upside down” when joystick is upright.

#### Step 23: Check for Shorts

Inspect the board and check that none of the connections are shorted. There should be no bridges/connections between adjacent pins. If you have a multimeter, you can use it to double check continuity. | WARNING: If pins are shorted they may damage the USB port on your computer.

#### Step 24: Insert M3 Hex Nuts into Enclosure

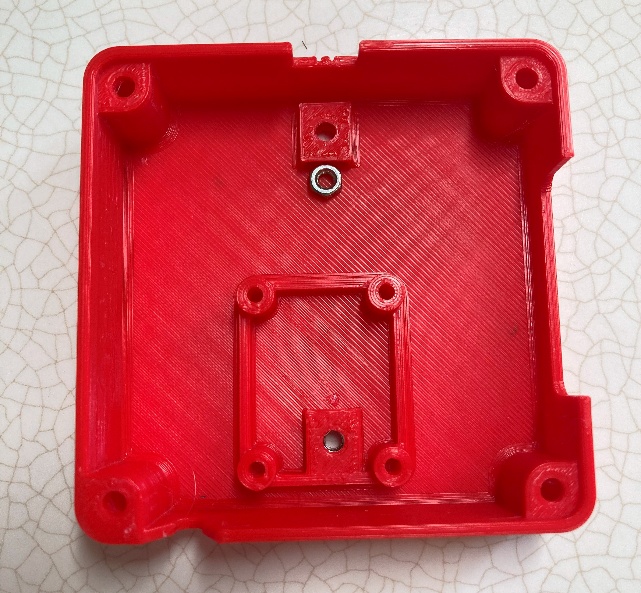
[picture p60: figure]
Bottom of enclosure with M3 nut being inserted.

Insert M3 nuts into captive nut slots. You might need to use pliers to push the nuts in.

#### Step 25: Insert Switch Cover

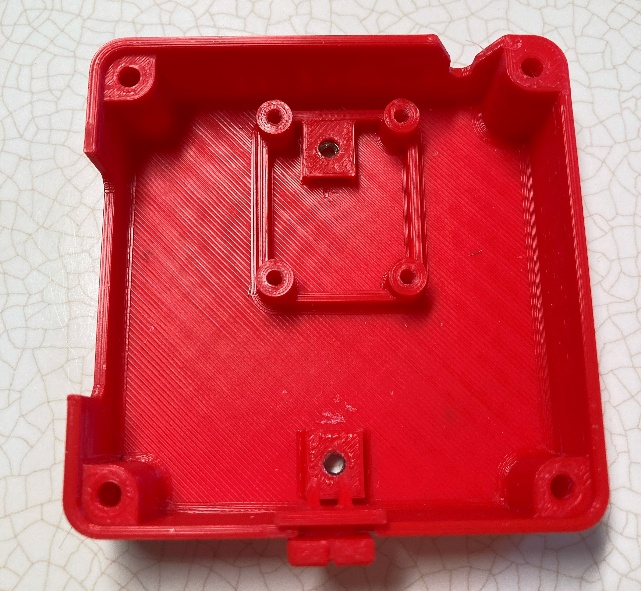
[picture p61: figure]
Bottom of enclosure with slide switch installed.

Place the slide switch cover in the slot with the taller side/slot up.

#### Step 26: Plug in USB-C Cable and Insert 3D PCB into Enclosure

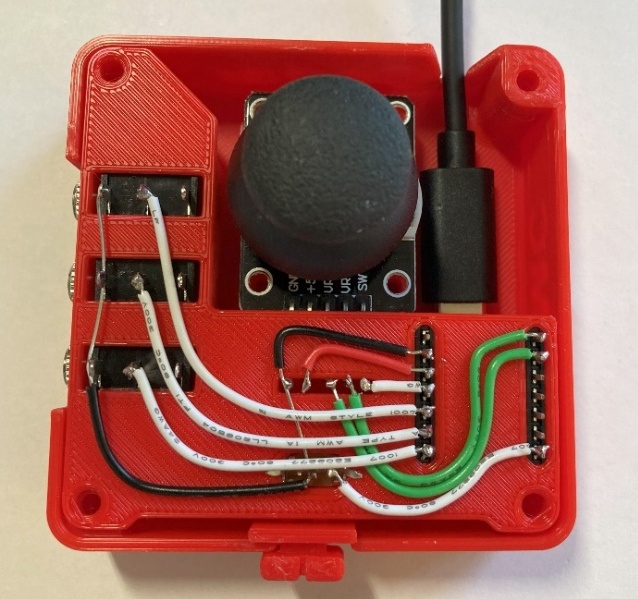
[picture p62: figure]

Plug the USB-C cable into the Adafruit QT Py board. Insert the 3D PCB into bottom of enclosure, the joystick should sit on the 4 posts. You may need to move the slide switch cover so that it lines up with the slide switch and fits onto it. Insert screws into the joystick board’s 4 screw holes.

#### Step 27: Assemble Enclosure

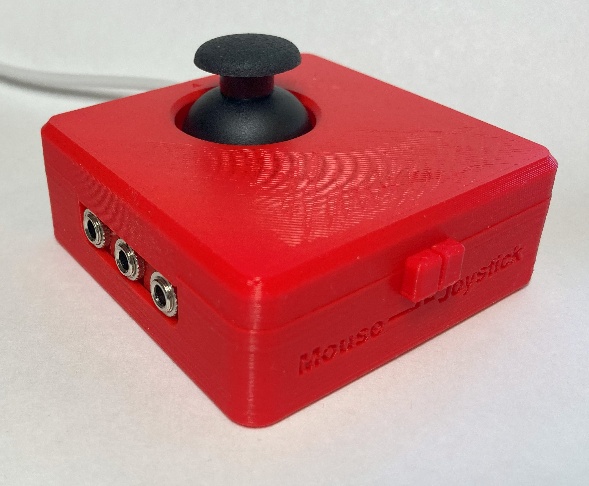
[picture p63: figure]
Assembled joystick, isometric view.
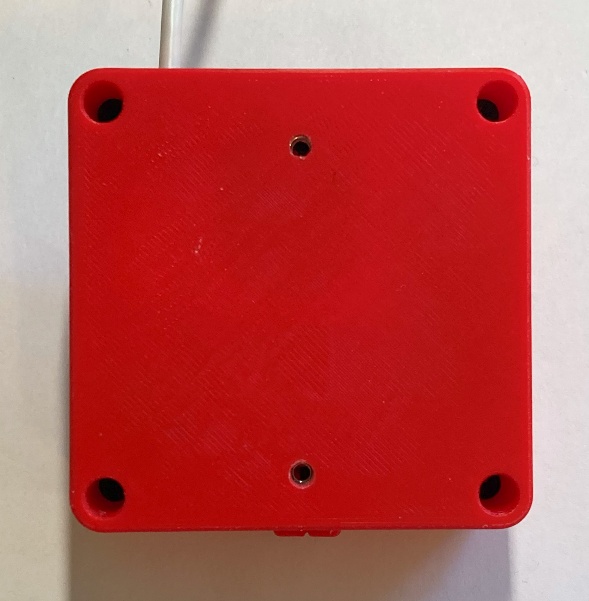
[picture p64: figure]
Bottom of assembled joystick, showing 4 screw holes.

Place the top onto the enclosure. Screw in all 4 screws from the bottom.

## Part B: Flashing Firmware to Joystick

#### Step B01: Setup Arduino IDE

  1.1. Download Arduino IDE for your operating system at https://www.arduino.cc/en/software
  1.2. Install Arduino IDE

#### Step B02: Setup Core

  1.3. Open Arduino IDE.
  1.4. Click on File -> Preferences
  1.5. Locate the text field that says Additional Boards Manager URLs beside it.
  1.6. Copy and paste the following link into the field as a new line: https://adafruit.github.io/arduino-board-index/package_adafruit_index.json
  1.7. Click on OK.
  1.8. Restart the Arduino IDE.
  1.9. Open the Boards Manager option from the Tools-> Board-> Boards Manager..., search for “Adafruit SAMD” and select “Adafruit SAMD Boards” by Adafruit.

#### Step B03: Install Libraries

  1.10. Go to https://github.com/cyborg5/TinyUSB_Mouse_and_Keyboard and go to Code -> Download ZIP and then rename this ZIP folder “TinyUSB_Mouse_and_Keyboard”.
  1.11. In the Arduino IDE, go to Sketch -> Include Library -> Add .ZIP library and then select the “TinyUSB_Mouse_and_Keyboard” ZIP folder (likely found in your Downloads).
  1.12. Go to Tools -> Manage Libraries…, search for “Flash Storage” and install the library “FlashStorage” by Arduino.

#### Step B04: Upload the Code to the joystick

  1.13. Open OpenAT_Joystick_Mouse_M0_Software_Cedar.ino with Open Arduino IDE.
  1.14. Select Adafruit QT Py M0 (SAMD21) from Tools -> Board -> Adafruit SAMD Boards
  1.15. Click on Tools -> USB Stack and select Adafruit TinyUSB
  1.16. Connect the joystick using the USB cable to the computer.
  1.17. Select the correct port from Tools -> Port menu.
  1.18. Verify and upload the code.

# Testing

1. Slide the Mode Switch to Joystick mode.
2. Connect the joystick using the USB cable to the computer.
3. If using Windows, open “Set up USB Game Controllers” from the Control Panel. You can find this by searching your computer in the search bar next to the Windows icon.
4. Ensure that the joystick is registered as a game controller and select your joystick from the list and go to “Properties”.
5. Move your joystick and observe the movement of the cross hatch in the “Axes” window. Ensure it moves in the proper directions when you move the joystick (the arrow points in the up direction). If not, open the joystick and check your connections.
6. Using assistive switches plugged into each mono jack, activate each switch, and ensure that one of buttons 1-4 light up when you press the switch, and stops when you release the switch. If not, open the joystick and check your connections.

If you wish to test the joystick in Mouse mode, slide the mode switch to Mouse mode before plugging the joystick into the computer. In mouse mode, the joystick should move the cursor and the three switches (A, B, C) should act as left click, middle click, and right click respectively.

Important note: the mode can only be changed before plugging in the joystick to the host device. If the mode switch is changed while the joystick is plugged in, it will have no effect.

[^1] https://www.printables.com/model/501869-analog-thumbstick-topper-collection

© 2026 by Neil Squire This work is licensed under the CC BY SA 4.0 License: http://creativecommons.org/licenses/by-sa/4.0 Files available at https://github.com/makersmakingchange/Cedar-Mini-Joystick Page 1 of 1

V1.1 | JULY 2026 Cedar USB Joystick maker Guide

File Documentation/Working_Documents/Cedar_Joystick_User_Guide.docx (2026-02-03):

# Overview

This document contains the necessary information to use the Cedar USB Joystick, a joystick with switch ports.

A photo of a fully assembled Cedar USB Joystick.

## Contents

## Introduction

The Cedar is a small USB joystick that can act as a mouse or an HID Gamepad. It connects directly to a compatible device via the integrated USB cable. The mode can be changed by sliding a switch on the enclosure. The joystick can be pressed down as an input, and up to 3 assistive switches can be connected using the 3.5 mm input jacks.

The joystick has a range of motion of ±30° and requires approximately 75 grams-force to fully deflect.

## Features

USB Cable

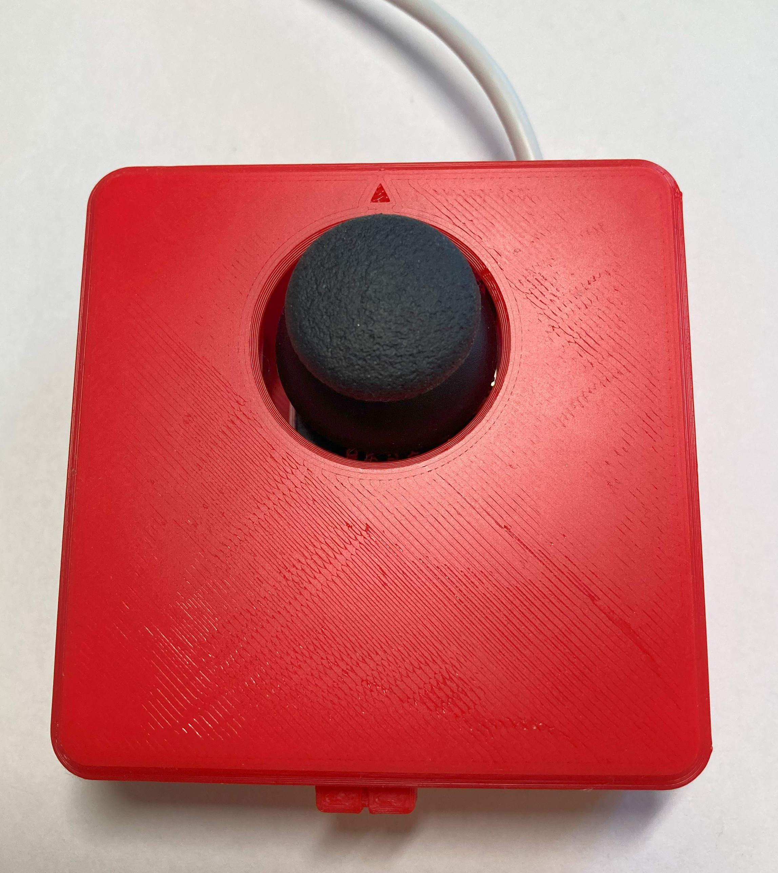
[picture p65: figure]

Joystick

Arrow indicating “up” direction on joystick

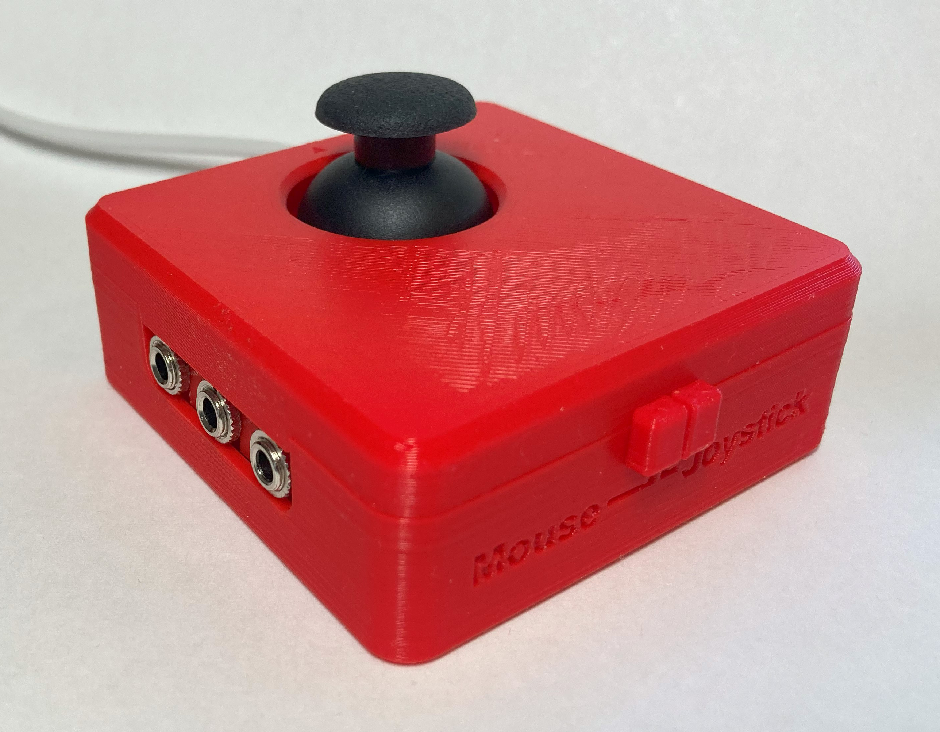
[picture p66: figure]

External Assistive Switch Inputs

Mode Switch

### Mode Switch

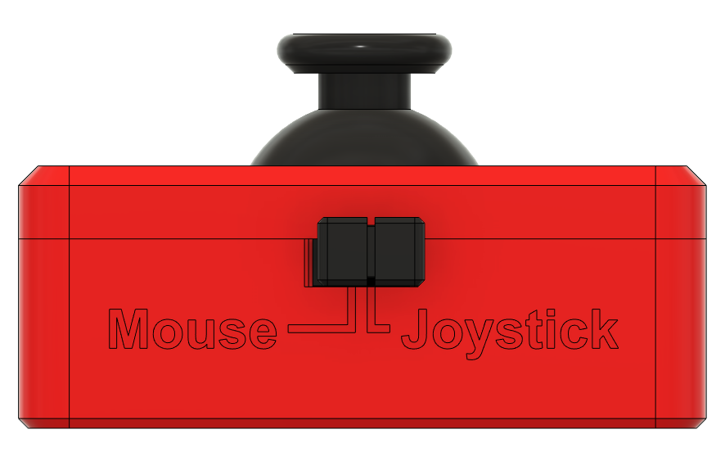
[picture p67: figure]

### External Assistive Switch Inputs

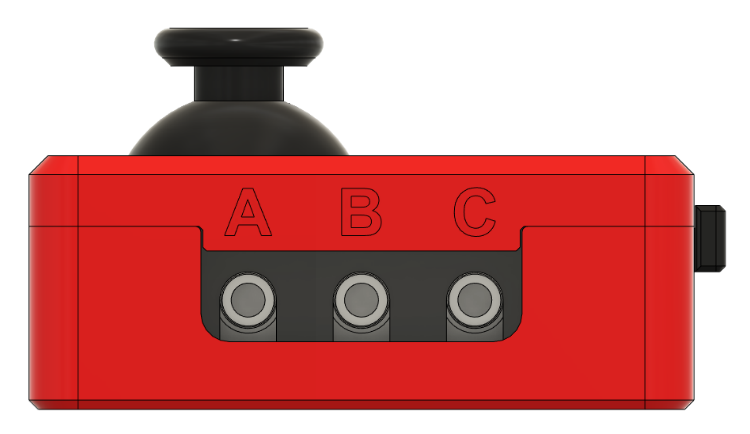
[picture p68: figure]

There are three 3.5 mm (1/8 in.) jacks on the side of the joystick for connecting external assistive switches. They are labelled from left to right as A, B, C.

### Mounting Holes

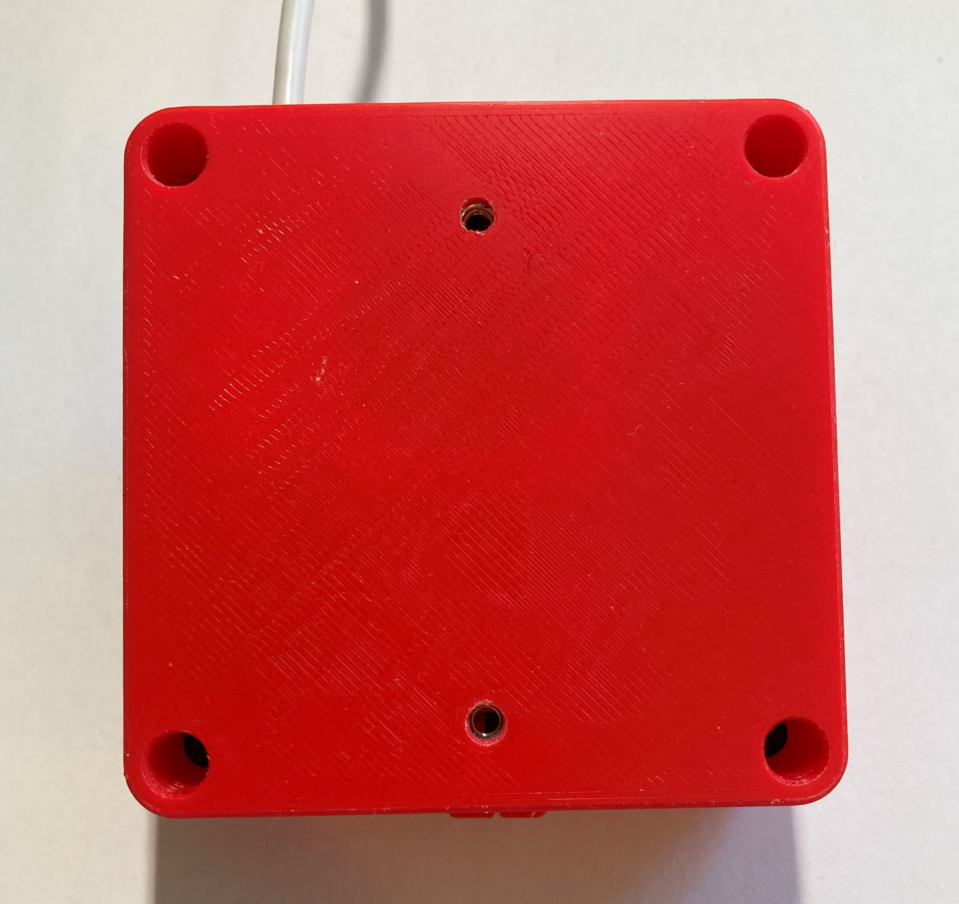
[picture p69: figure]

Screw holes for mount adapters

## Compatibility

Mouse mode – compatible with PC, most Android phones and tablets, and Apple phones and tablets with iOS13 and iPadOS.

Joystick mode – compatible with PC (direct or gaming with Steam), most Android phones and tablets, and Apple phones and tablets with iOS13 and iPadOS, and with Xbox Adaptive Controller (XAC). Through the XAC it is compatible with PC and Xbox directly, or can be used with other gaming consoles with adapters.

## Usage

For Mouse Mode:

1. Move the slide switch to the left for Mouse Mode, as indicated on the housing.
2. Plug in assistive switches to the switch jacks. The default switch mapping is stated below.
3. Plug the joystick into the device you wish to use it with.
4. Orient the joystick so the arrow on top is facing away from the user and the cable is exiting the enclosure away from the user.
5. Move the joystick to move the mouse, use the switches for the functions listed below.

For Joystick Mode:

1. Move the slide switch to the right for Joystick Mode, as indicated on the housing.
2. If desired, plug in assistive switches to the switch jacks. The default switch mapping is stated below.
3. Plug the joystick into the device you wish to use it with.
4. Orient the joystick so the arrow on top is facing away from the user and the cable is exiting the enclosure away from the user.
5. Move the joystick to move the mouse, use the switches for the functions listed above.
6. Depending on what device you are using the joystick with, if you are using switches plugged into the jacks you will most likely want to remap them. This can be done in your system’s settings.

To Switch Modes:

1. Disconnect the joystick from the host device by unplugging the USB Cable.
2. Slide the Mode Switch to the desired mode.
3. Reconnect the joystick to the host device by plugging in the USB Cable.

### Input Mapping

Cedar | Mouse Mode | Joystick Mode
| | PC | XAC (Left USB) | XAC (Right USB)
Joystick | Cursor movement | Joystick | Left thumbstick | Right thumbstick
A | Left click | Button 1 | X1 | View
B | Middle click (scroll) | Button 2 | X2 | Menu
C | Right click | Button 3 | Left stick (left press) | Right stick (right press)
Joystick push down | Left click | Button 4 | Left bumper | Right bumper

### Mounting

There are several options for positioning or mounting the joystick.

#### Tabletop – Non-slip pads

Nonslip pads or sheet (e.g., DYCEM) can be used to prevent the joystick from slipping on a tabletop or other hard surface.

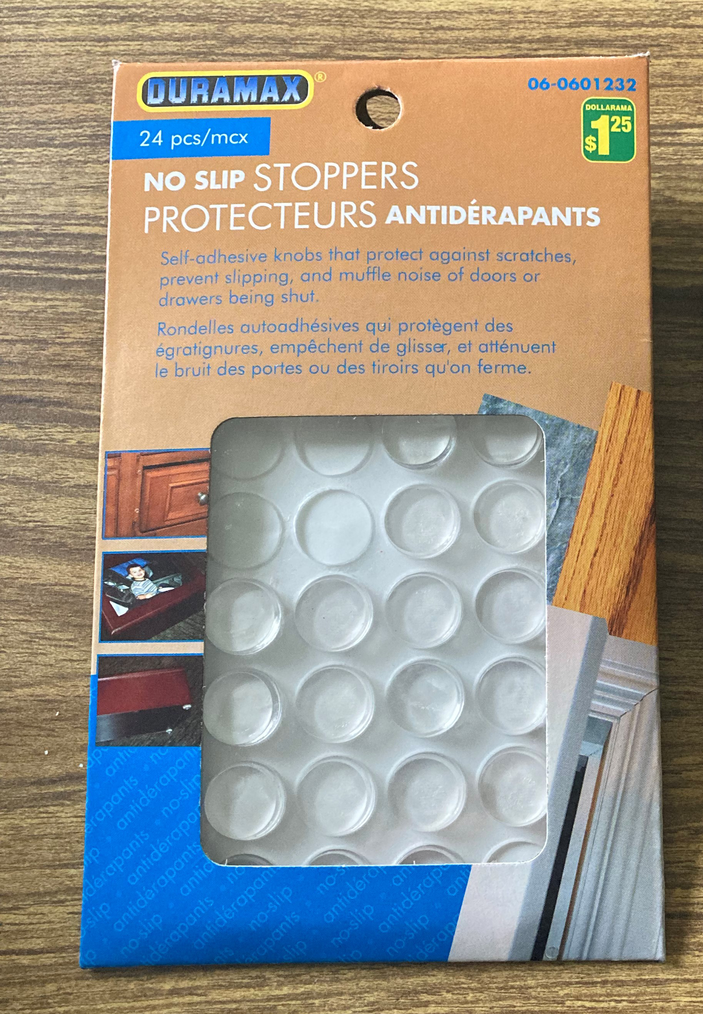
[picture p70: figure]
A pack of "No Slip Stoppers". They are small clear plastic circles.
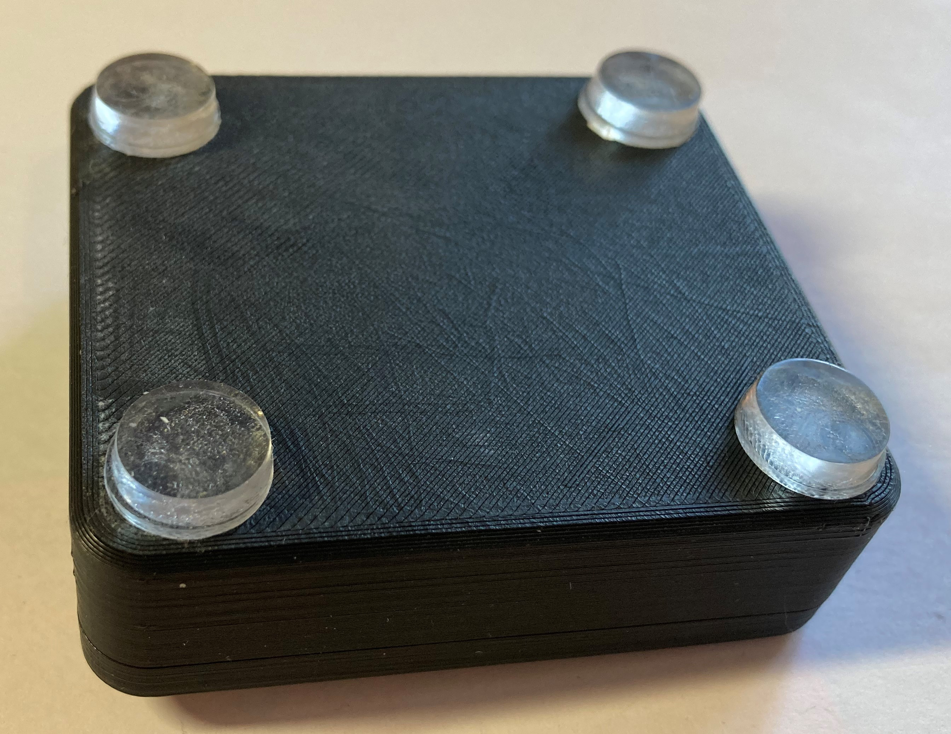
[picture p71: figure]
The bottom of the joystick, with 4 no slip stoppers on the bottom.

#### Tabletop – Hook and Loop Fastener

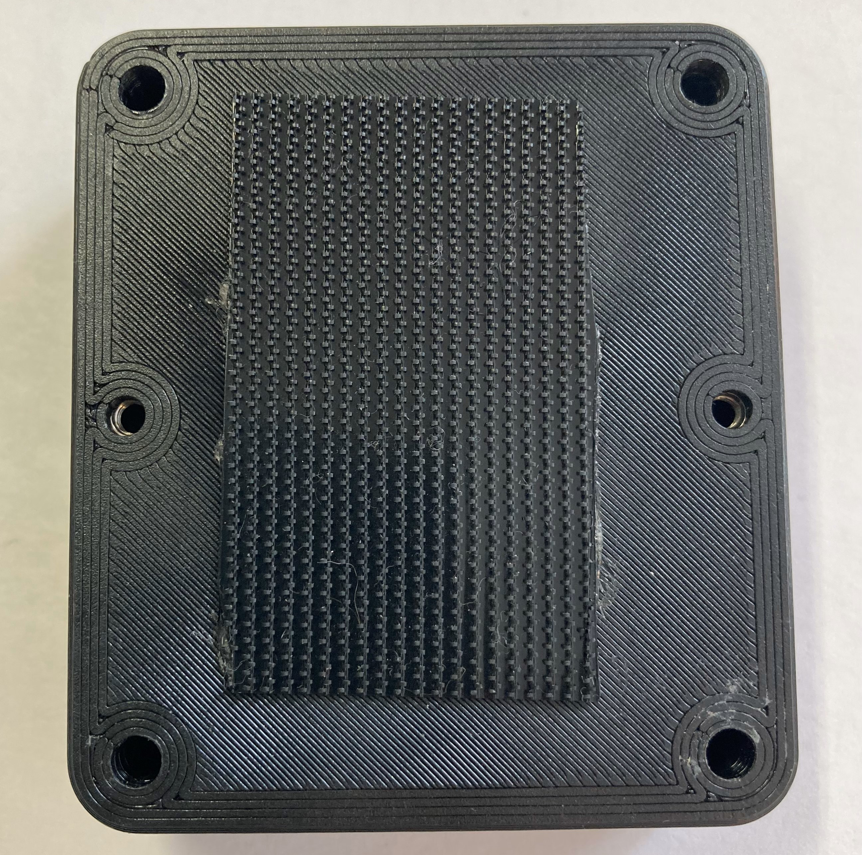
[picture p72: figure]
Bottom of the joystick with hook and loop fastener attached to the bottom. The hook side is shown stuck to the joystick.

For more permanent use on a tabletop or other surface such as a lap tray, use hook and loop fastener (e.g., VELCRO). Typically, best practice is to stick the side with the loops (the softer side) to the tabletop or other surface, and to stick the side with the hooks (rough side) to the joystick.

#### Camera / Tripod Mount (¼-20 UNC thread)

The joystick can be mounted using a range of commercial and DIY mounting arms by using the Camera Mount Adapter. The Camera Mount Adapter is attached to the bottom of the Joystick enclosure using two M3 screws that are at least 10 mm long and provides an internal ¼-20 UNC thread that can be attached to tripod mounts and other mounting solutions with an external ¼-20 UNC thread.

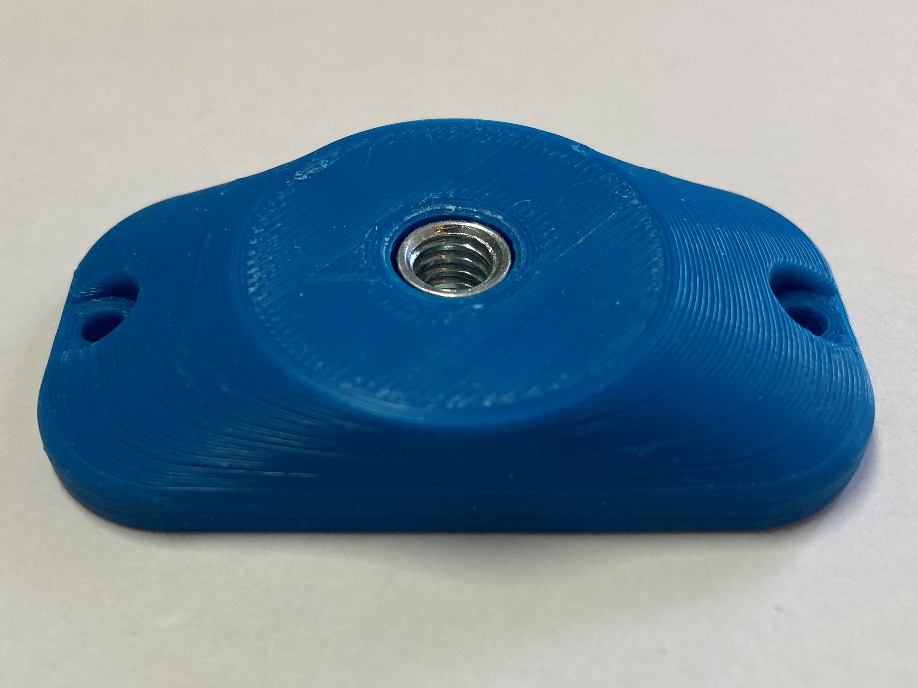
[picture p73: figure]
Camera mount adapter for the joystick, top view. Made from blue plastic with a metal tee nut insert, with 1/4-20 thread.
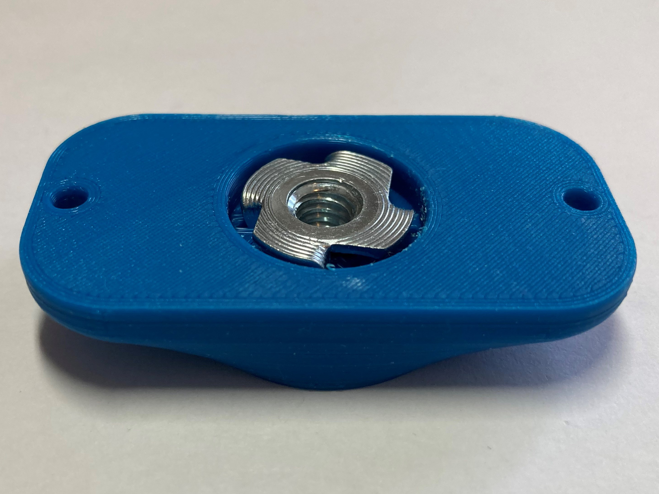
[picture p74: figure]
Camera mount adapter for the joystick, bottom view. Made from blue plastic with a metal tee nut insert, with 1/4-20 thread.
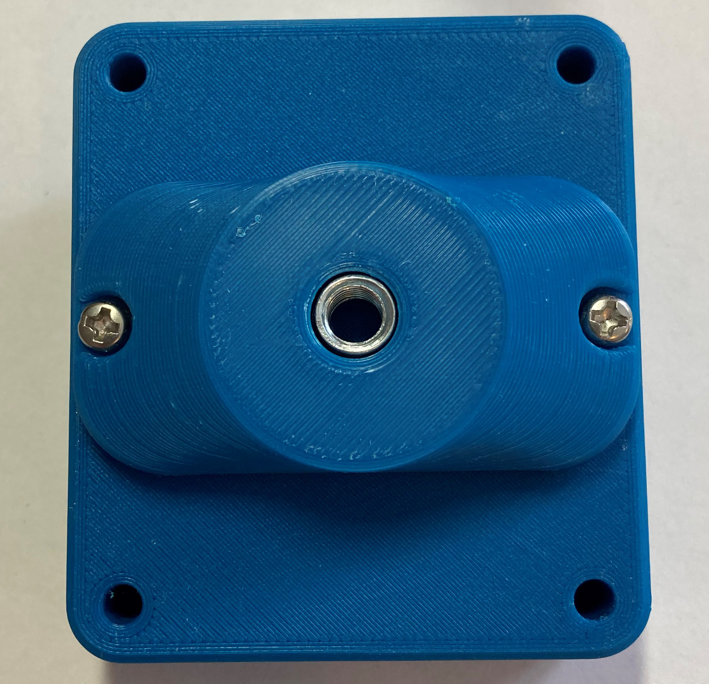
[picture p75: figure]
The camera mount adapter installed on the bottom of the Birch Mini Joystick.

Now, the joystick can be mounted on a mount with ¼-20 thread, such as a typical camera mount.

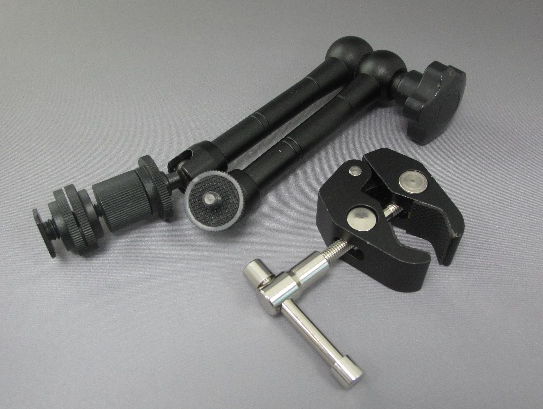
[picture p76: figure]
A commercially available magic arm with a clamp on one end and a 1/4-20 UNC thread on the other.

#### RAM Mount (1 inch/RAM B)

When mounting on a RAM B compatible mount, the RAM Mount Adapter can be attached to a joystick using two M3 screws that are at least 10 mm long.

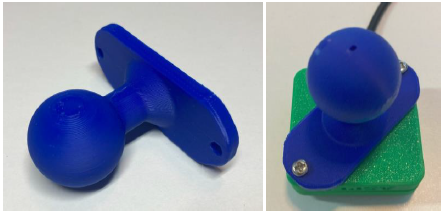
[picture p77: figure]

## Specifications

Joystick Range of Motion | ± 30°
Joystick Range of Motion at Tip | ± 15 mm
Joystick Activation Force | 75 grams
Total height (with default topper) | 40 mm
Enclosure height | 27 mm
Enclosure width | 70 mm
Enclosure length | 70 mm

## Cleaning

The Cedar USB Joystick can be wiped down with a damp cloth. Do not use hot water on this device or the plastic housing may warp. Do not submerge the device.

© 2026 by Neil Squire This work is licensed under the CC BY SA 4.0 License: http://creativecommons.org/licenses/by-sa/4.0 Files available at https://github.com/makersmakingchange/Cedar-Mini-Joystick Page 2 of 3

V1.0 | SEPTEMBER 2025 Cedar USB Joystick user Quick Guide

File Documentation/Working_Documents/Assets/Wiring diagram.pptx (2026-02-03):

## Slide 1

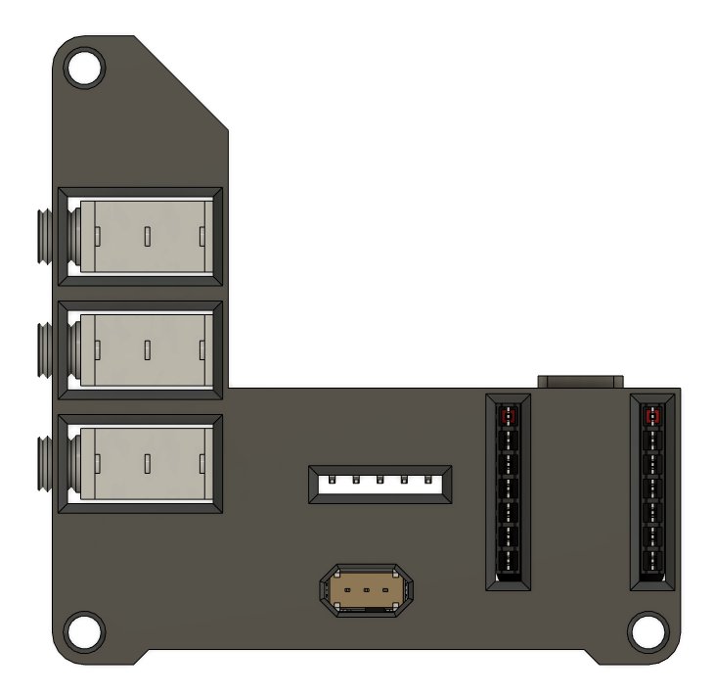
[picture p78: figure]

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
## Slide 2

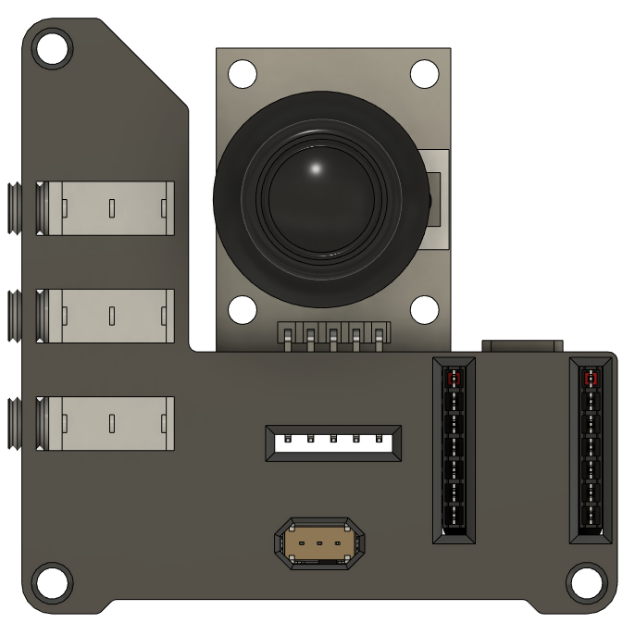
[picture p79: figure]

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
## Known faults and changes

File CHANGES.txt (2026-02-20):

------CEDAR MINI JOYSTICK------
           Changelog
===============================
Version 1.0 | 2026-02-20
 - Initial release
 - Updated documentation
    - Finalized Maker Guide
    - Update User Guide and BOM
    - Created Summary document

Version 0.9 | 2023-Jun-30
 - Initial commit
 - Cedar Mini joystick with 3 integrated switch jacks and a mode slide switch
 - Firmware has Mouse mode and Joystick mode

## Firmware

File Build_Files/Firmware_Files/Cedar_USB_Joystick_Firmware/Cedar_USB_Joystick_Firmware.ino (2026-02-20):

/* 
* File: Cedar_USB_Joystick_Firmware.ino
* Software: Cedar USB Joystick Plus 4 Switches, with both USB gamepad and mouse funtionality.
* Developed by: Makers Making Change
* Version: (12 July 2023) 
  License: GPL v3

  Copyright (C) 2023-2026 Neil Squire Society
  This program is free software: you can redistribute it and/or modify it under the terms of
  the GNU General Public License as published by the Free Software Foundation,
  either version 3 of the License, or (at your option) any later version.
  This program is distributed in the hope that it will be useful, but WITHOUT ANY WARRANTY;
  without even the implied warranty of MERCHANTABILITY or FITNESS FOR A PARTICULAR PURPOSE.
  See the GNU General Public License for more details.
  You should have received a copy of the GNU General Public License along with this program.
  If not, see <http://www.gnu.org/licenses/>
*/
#include <FlashStorage.h>
#include "XACGamepad.h"
#include <TinyUSB_Mouse_and_Keyboard.h>

#define MODE_MOUSE 1
#define MODE_GAMEPAD 0

#define UPDATE_INTERVAL   5 // Update interval for perfoming HID actions (in milliseconds)
#define DEFAULT_DEBOUNCING_TIME 5

#define JOYSTICK_DEFAULT_DEADZONE_LEVEL      1 // Joystick deadzone
#define JOYSTICK_MIN_DEADZONE_LEVEL          1 // 
#define JOYSTICK_MAX_DEADZONE_LEVEL          10
#define JOYSTICK_MAX_DEADZONE_VALUE          64 // Out of 127
#define JOYSTICK_MAX_VALUE                   127 

#define JOYSTICK_REACTION_TIME               30 // Minimum time between each action in ms
#define SWITCH_REACTION_TIME                 100 // Minimum time between each switch action in ms

#define SLOW_SCROLL_DELAY                    200 // Minimum time, in ms, between each slow scroll action (number of slow scroll actions defined below)
#define FAST_SCROLL_DELAY                    60 // Minimum time, in ms, between each fast scroll action (higher delay = slower scroll speed)
#define SLOW_SCROLL_NUM                      10 // Number of times to scroll at the slow scroll rate

#define MOUSE_MAX_XY                         6 // Amount to move mouse at max deflection (max "speed")

//Define model number and version number
#define JOYSTICK_MODEL                        1
#define JOYSTICK_VERSION                      2

//Define Joystick Analog pins
#define JOYSTICK_X_PIN                        A0
#define JOYSTICK_Y_PIN                        A1  

#define SWITCH_A_PIN      9 
#define SWITCH_B_PIN      8 
#define SWITCH_C_PIN      7 
#define SWITCH_JOY_PIN    10 // Switch built int the joystick (press down)

#define SWITCH_MODE_PIN   6 // Slide switch for mode

XACGamepad gamepad;  // Starts an instance of the USB gamepad object

// Declare variables for settings
int isConfigured; 
int modelNumber;
int versionNumber;
int deadzoneLevel;

FlashStorage(isConfiguredFlash, int);
FlashStorage(modelNumberFlash, int);
FlashStorage(versionNumberFlash, int);
FlashStorage(deadzoneLevelFlash, int);

long lastInteractionUpdate;

// Declare joystick input and output variables 
int inputX;
int inputY;
int outputX;
int outputY;

//Declare switch state variables for each switch
int switchAState;           // Mouse mode = left click
int switchBState;           // Mouse mode = scroll mode
int switchCState;           // Mouse mode = right click
int switchJoyState;         // Mouse mode = left click              // Switch in the joystick (press down)

int operatingMode;  // 1 = Mouse mode, 0 = Joystick mode

//Previous status of switches
int switchAPrevState = HIGH;          
int switchBPrevState = HIGH;
int switchCPrevState = HIGH;
int switchJoyPrevState = HIGH;

int currentDeadzoneValue;

bool settingsEnabled = false;

//***API FUNCTIONS***// - DO NOT CHANGE
typedef void (*FunctionPointer)(bool, bool, String);      

//Type definition for API function pointer

typedef struct {                                  //Type definition for API function list
  String endpoint;                                //Unique two character end point
  String code;                                    //Unique one character command code
  String parameter;                               //Parameter that is passed to function
  FunctionPointer function;                       //API function pointer
} _functionList;

//Switch structure 
typedef struct { 
  uint8_t switchNumber;
  String switchButtonName;
  uint8_t switchButtonNumber;
} switchStruct;


// Declare individual API functions with command, parameter, and corresponding function
_functionList getModelNumberFunction =            {"MN", "0", "0", &getModelNumber};
_functionList getVersionNumberFunction =          {"VN", "0", "0", &getVersionNumber};
_functionList getJoystickDeadZoneFunction =       {"DZ", "0", "0", &getJoystickDeadZone};
_functionList setJoystickDeadZoneFunction =       {"DZ", "1", "",  &setJoystickDeadZone};

// Declare array of API functions
_functionList apiFunction[5] = {
  getModelNumberFunction,
  getVersionNumberFunction,
  getJoystickDeadZoneFunction,
  setJoystickDeadZoneFunction
};

//Switch properties 
const switchStruct switchProperty[] {
    {1,"A",1},
    {2,"B",2},
    {3,"C",3},
    {4,"Joy",4}
    
};

//***MICROCONTROLLER AND PERIPHERAL CONFIGURATION***//
// Function   : setup 
// 
// Description: This function handles the initialization of variables, pins, methods, libraries. This function only runs once at powerup or reset.
// 
// Parameters :  void
// 
// Return     : void
//*********************************//
void setup() {
  
  // Check if mouse or joystick mode
  pinMode(SWITCH_MODE_PIN, INPUT_PULLUP);
  operatingMode = digitalRead(SWITCH_MODE_PIN);

/*
  // Begin HID gamepad or mouse, depending on mode selection
  if (isMouseMode){
    Mouse.begin();
  } else{
    gamepad.begin();
  }
*/
  // Begin HID gamepad or mouse, depending on mode selection
  switch(operatingMode) {
    case MODE_MOUSE:
      Mouse.begin();
      break;
    case MODE_GAMEPAD:
      gamepad.begin();
      break;
  }
    
  delay(5000);
  // Initialize Memory   
  initMemory();
  
  delay(5);

  // Initialize Joystick 
  initJoystick();

  // Begin serial
  Serial.begin(115200);

  //Initialize the switch pins as inputs
  pinMode(SWITCH_A_PIN, INPUT_PULLUP);    
  pinMode(SWITCH_B_PIN, INPUT_PULLUP);   
  pinMode(SWITCH_C_PIN, INPUT_PULLUP);   
  pinMode(SWITCH_JOY_PIN, INPUT_PULLUP);   

  lastInteractionUpdate = millis();  // get first timestamp

}

void loop() {

    settingsEnabled=serialSettings(settingsEnabled); //Check to see if setting option is enabled
    

  if (millis() >= lastInteractionUpdate + UPDATE_INTERVAL) {    
    lastInteractionUpdate = millis();  // get timestamp
    readJoystick();
    readSwitches();

    joystickActions();

    switch(operatingMode) {
      case MODE_MOUSE:
        switchesMouseActions();
        break;
      case MODE_GAMEPAD:
        switchesJoystickActions();
        break;
    }
  }
}

//*********************************//
// Joystick Functions
//*********************************//

//***INITIALIZE Memory FUNCTION***//
// Function   : initMemory 
// 
// Description: This function initializes Memory
//
// Parameters : void
// 
// Return     : void 
//****************************************//
void initMemory() {
  //Check if it's first time running the code
  isConfigured = isConfiguredFlash.read();
  delay(5);
  
  if (isConfigured==0) {
    //Define default settings if it's first time running the code
    modelNumber=0;
    versionNumber=2;
    deadzoneLevel=6;
    isConfigured=1;

    //Write default settings to flash storage 
    modelNumberFlash.write(modelNumber);
    versionNumberFlash.write(versionNumber);
    deadzoneLevelFlash.write(deadzoneLevel);    
    isConfiguredFlash.write(isConfigured);
    delay(5);
      
  } else {
    //Load settings from flash storage 
    modelNumber=modelNumberFlash.read();
    versionNumber=versionNumberFlash.read();
    deadzoneLevel=deadzoneLevelFlash.read();    
    delay(5);
  }  

    //Serial print settings 
    Serial.print("Model Number: ");
    Serial.println(modelNumber);

    Serial.print("Version Number: ");
    Serial.println(versionNumber);
    
    Serial.print("Deadzone Level: ");
    Serial.println(deadzoneLevel);   
}

//***INITIALIZE JOYSTICK FUNCTION***//
// Function   : initJoystick 
// 
// Description: This function initializes joystick as input.
//
// Parameters : void
// 
// Return     : void 
//****************************************//
void initJoystick()
{
  getJoystickDeadZone(true,false);//Get joystick deadzone stored in memory    //Get joystick calibration points stored in flash memory 
}

//***READ JOYSTICK FUNCTION**//
// Function   : readJoystick
//
// Description: This function reads the current raw values of potentiometers, checks if values exceed deadband, and calculates
//              joystick movements. 
//
// Parameters :  Void
//
// Return     : Void
//*********************************//

void readJoystick() {

    //Read analog raw value using ADC
    inputX = analogRead(JOYSTICK_X_PIN);
    inputY = analogRead(JOYSTICK_Y_PIN);  

    //Map joystick x and y move values 
    outputX = map(inputX, 0, 1023, -127, 127);
    outputY = map(inputY, 0, 1023, -127, 127);

    double outputMag = calcMag(outputX, outputY);

    //Apply radial deadzone *********************************************************************
    if (outputMag<=currentDeadzoneValue) 
    {
      outputX = 0;
      outputY = 0;
    }

}

//***JOYSTICK ACTIONS FUNCTION**//
// Function   : joystickActions
//
// Description: This function executes joystick or mouse movements.
//
// Parameters :  Void
//
// Return     : Void
//*********************************//

void joystickActions() {

    switch(operatingMode) {
      case MODE_MOUSE:
        //mouse action
        Mouse.move(MOUSE_MAX_XY*outputX/127, -MOUSE_MAX_XY*outputY/127, 0);
        break;
      case MODE_GAMEPAD:
        //Perform joystick HID action 
        gamepadJoystickMove(outputX,outputY);
        break;
    }
    
    //delay(JOYSTICK_REACTION_TIME);
}

//***READ SWITCH FUNCTION**//
// Function   : readSwitches 
//
// Description: This function reads the current digital values of pull-up pins.
//
// Parameters :  Void
//
// Return     : Void
//*********************************//

void readSwitches(){
    // Update Prev Switch States
    switchAPrevState=switchAState;
    switchBPrevState=switchBState;
    switchCPrevState=switchCState;
    switchJoyPrevState=switchJoyState;

    //Update status of switch inputs
    switchAState = digitalRead(SWITCH_A_PIN);
    switchBState = digitalRead(SWITCH_B_PIN);
    switchCState = digitalRead(SWITCH_C_PIN); 
    switchJoyState = digitalRead(SWITCH_JOY_PIN); 
    
}

//***JOYSTICK MODE - SWITCH ACTIONS FUNCTION**//
// Function   : switchesJoystickActions
//
// Description: This function executes joystick functions of the switches.
//
// Parameters :  Void
//
// Return     : Void
//*********************************//

void switchesJoystickActions(){

    //Perform button actions
    if(!switchAState) {
     gamepadButtonPress(switchProperty[0].switchButtonNumber);
    }
    else if(switchAState && !switchAPrevState) {
      gamepadButtonRelease(switchProperty[0].switchButtonNumber);
   }
 
    if(!switchBState) {
      gamepadButtonPress(switchProperty[1].switchButtonNumber);
    } else if(switchBState && !switchBPrevState) {
      gamepadButtonRelease(switchProperty[1].switchButtonNumber);
    }
   
    if(!switchCState) {
      gamepadButtonPress(switchProperty[2].switchButtonNumber);
    } else if(switchCState && !switchCPrevState) {
      gamepadButtonRelease(switchProperty[2].switchButtonNumber);
    }

    if(!switchJoyState) {
      gamepadButtonPress(switchProperty[3].switchButtonNumber);
    } else if(switchJoyState && !switchJoyPrevState) {
      gamepadButtonRelease(switchProperty[3].switchButtonNumber);
    }

}
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

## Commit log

2023-07-05 Updated BOM
    [Cedar_Mini_Joystick_BOM.xlsx, Cedar_Mini_Joystick_BOM_v0.9.csv, Cedar_Mini_Joystick_BOM_v0.9.xlsx]
2023-07-18 Added labels to switch jacks
    [Enclosure_top.stl]
2024-01-18 Updated BOM and BOM list in Assembly Guide
    [Cedar_Mini_Joystick_BOM.xlsx, Cedar_Mini_Joystick_BOM_v0.9.csv, Cedar_Mini_Joystick_BOM_v0.9.xlsx]
2026-02-03 Delete Build_Files directory
    Deleting old files to replace with new finalized version 1 files.
    [3D_PCB.stl, Enclosure_bottom.stl, Enclosure_top.stl, Joystick_Camera_Mount_Adapter v0.2.stl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]
2026-02-03 Delete Documentation directory
    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
    [Cedar_Mini_Joystick_BOM.xlsx, Cedar_Mini_Joystick_BOM_v0.9.csv, Cedar_Mini_Joystick_BOM_v0.9.xlsx]
2026-02-03 Delete Design_Files directory
    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
    [3D PCB.f3d, Enclosure bottom.f3d, Enclosure top.f3d, Switch_Slide v5.f3d]
2026-02-03 v1.0 documentation
    Uploading documentation for publishing
    [Cedar_Joystick_BOM.csv, Cedar_Joystick_BOM.xlsx]
2026-02-19 Remove spaces from CAD filenames
    [3D PCB.step, 3D_PCB.f3d, 3D_PCB.step]
2026-04-02 Mounting adapter removed
    Removed mounting adapter from 3D print files and updated the readme to include a link to the mounting adapters
    [Joystick_Camera_Mount_Adapter.stl]
